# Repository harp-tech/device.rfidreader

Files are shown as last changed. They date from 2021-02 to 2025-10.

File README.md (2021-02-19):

# Harp RFID reader

RFID reader for 125KHz carriers.
Compible with glass capsules, buttons and cards (check pics folder).

# Licensing

The code, designs, documentation, and photos available in this repository is free: you can redistribute it and/or modify it under the terms of the used license.
Each subdirectory will contain a license or, possibly, a set of licenses if it involves both hardware and software. Check files named LICENSE.

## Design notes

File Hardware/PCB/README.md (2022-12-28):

## Licensing

The designs, documentation, and photos available in this repository are free: you can redistribute it and/or modify it under the terms of the used license.
Check file named LICENSE.

Copyright Filipe Carvalho 2021-2022

<br />This work is licensed under a <a rel="license" href="http://creativecommons.org/licenses/by-nc-sa/3.0/igo/">Creative Commons Attribution-NonCommercial-ShareAlike 3.0 IGO License</a>.

If your are interested in obtaining a license to sell this device, please contact filipe@oeps.tech

[1]: https://docs.google.com/spreadsheets/d/1aobmmEzBDethzIlrm1eg0eYkBqlyX3s9WbA9KgRwVQI/edit?usp=sharing

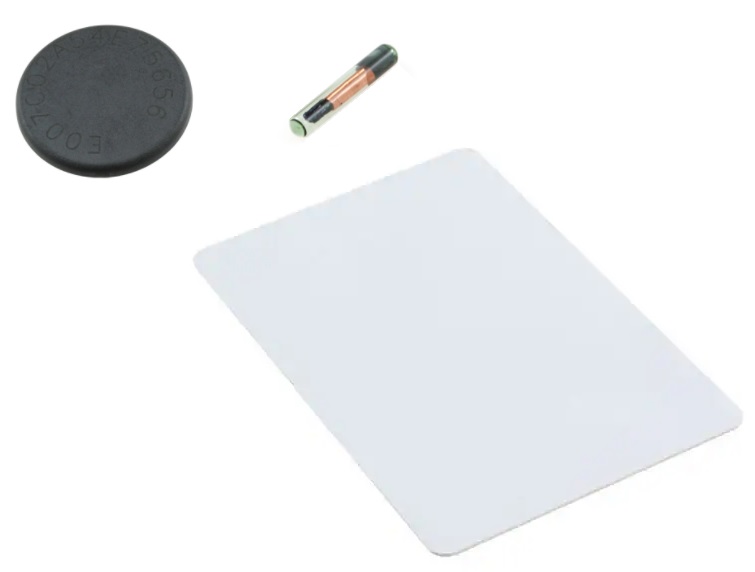
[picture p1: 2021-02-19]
Assets/compatible types of tags.jpg

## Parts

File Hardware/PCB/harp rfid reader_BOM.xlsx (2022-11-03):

Qty | Value | Package | Parts | MPN | Type | Distributor | Distributor PN
ASSEMBLY HOUSE
2 | 47pF | C0402 | C3, C4 | 04025A470JAT2A | SMD | Digikey | 478-1078-6-ND
1 | 4.7nF | C0402 | C1 | 885012205084 | SMD | Digikey | 732-12234-6-ND
11 | 100nF 50V X7R 10% | C0402 | C2, C6, C8, C9, C10, C12, C13, C14, C15, C16, C21 | CGA2B3X7R1H104K050BB | SMD | Digikey | 445-6899-6-ND
4 | 10uF 20% 16V X5R | C0603 | C5, C7, C11, C17 | EMK107BBJ106MA-T | SMD | Digikey | 587-3238-6-ND
3 | 100uF 20% 10V | CT3216 | C18, C19, C20 | TLJA107M010R1400 | SMD | Digikey | 478-5651-6-ND
1 | 39Ω 1/5watt 1% 0402 | R0402 | R7 | RCS040239R0FKED | SMD | Digikey | 541-10407-6-ND
5 | 1k | R0402 | R2, R3, R4, R6, R8 | CRCW04021K00FKED | SMD | Digikey | 541-1.00KLDKR-ND
1 | 10k | R0402 | R5 | CRCW040210K0FKED | SMD | Digikey | 541-10.0KLDKR-ND
1 | 1M | R0402 | R1 | CRCW04021M00FKED | SMD | Digikey | 541-1.00MLDKR-ND
1 | 40ohms 100MHz 1.5A 0805 SMD | L0805 | L1 | MI0805K400R-10 | SMD | Digikey | 240-2389-6-ND
1 | TRANS NPN 45V 0.5A | SC70-3 | Q1 | BC817-40W-7 | SMD | Digikey | BC817-40WDIDKR-ND
1 | MOSFET P-CH 60V 1.7A | SOT223 | Q2 | NTF2955T1G | SMD | Digikey | NTF2955T1GOSDKR-ND
4 | RED LED | LED0603 | TAG_B, TAG_T, STATE, OUT0 | 5975004407F | SMD | Digikey | 350-2950-6-ND
1 | Buzzers Transducer 3V 100mA 4kHz 78dB @ 3V |  | SP1 | SMT-0540-S-R | SMD | Digikey | 668-1060-6-ND
1 | USB to UART USB 2.0 | 28-SSOP | IC1 | FT232RL-REEL | SMD | Digikey | 768-1007-6-ND
1 | Ultra-Low-Noise LDO 3.3V 250mA | SOT-23-5 | IC2 | LP5907MFX-3.3/NOPB | SMD | Digikey | 296-38557-6-ND
1 | ATXMEGA32A4U | 44-TQFP | IC3 | ATXMEGA32A4U-A | SMD | Digikey | ATXMEGA32A4U-AURDKR-ND
1 | IC BUFFER NON-INVERT 5.5V | TSOP-5 | IC4 | M74VHC1GT126DT1G | SMD | Digikey | M74VHC1GT126DT1GOSDKR-ND
1 | 32 MHz CMOS | 4-SMD | OSC1 | O 32,0-JT32C-A-K-3,3-LF | SMD | Digikey | 1908-1044-6-ND
1 | CONN RCPT USB2.0 MINI |  | USB | UX60-MB-5S8 | SMD | Digikey | H2960DKR-ND
1 | CONN RCPT 5POS 0.1 GOLD SMD |  | U1 5POS | NPPN051BFLD-RC‎ | SMD | Digikey | ‎S5902-05-ND‎
1 | CONN RCPT 7POS 0.1 GOLD SMD |  | U1 7POS | ‎NPPN071BFLC-RC‎ | SMD | Digikey | ‎S5901-07-ND‎
1 | CONN Terminal block 2.54MM |  | OUT | 282834-2 | TH | Digikey | A98333-ND
POST-PRODUCTION
1 | RFID Reader ID-12LA (125 kHz) |  |  | ID-12LA | TH | SparkFun | SEN-11827
NOTES
 |  |  |  | Number of unique parts | 23
 |  |  |  | Number of SMD parts | 45
 |  |  |  | Number of TH parts | 1

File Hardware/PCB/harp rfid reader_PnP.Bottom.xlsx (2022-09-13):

C11 | 25.09 | 21.83 | 0 | 10uF | C0603
C12 | 23.55 | 2.46 | 270 | 100nF | C0402
C13 | 9.65 | 14.7 | 0 | 100nF | C0402
C14 | 19.72 | 20.88 | 90 | 100nF | C0402
C15 | 27.38 | 9.9 | 180 | 100nF | C0402
C16 | 16.8 | 3.37 | 270 | 100nF | C0402
C18 | 28.19 | 19.41 | 180 | 100uF | CT3216
C19 | 34.42 | 19.42 | 180 | 100uF | CT3216
C20 | 9.91 | 23.19 | 270 | 100uF | CT3216
C5 | 25.09 | 24.12 | 0 | 10uF | C0603
IC2 | 28.9 | 22.72 | 180 | LP5907MFX-3.3 | TSOT23-5
IC3 | 18.12 | 12.3 | 180 | ATXMEGA32A4U-AU | QFP80P1200X1200X120-44N
OSC1 | 20.29 | 2.38 | 0 | CNP-MISCELLANEOUS_OSCILLATOR | CNP-MISCELLANEOUS_OSCILLATOR_3.2X2.5
OUT0 | 40.55 | 19.45 | 270 |  | CHIP-LED0603
Q2 | 28.27 | 4.56 | 0 |  | SOT223
R3 | 25.6 | 11.16 | 90 | 1k | R0402
R4 | 21.79 | 23.86 | 0 | 1k | R0402
R7 | 34.83 | 8.8 | 180 | 75 >1/4W | R0402
SP1 | 33.92 | 13.45 | 0 | BUZZER-COIL_SMT-0540-S-R | BUZZER-COIL_SMT-0540-S-R
STATE | 25.6 | 13.45 | 180 |  | CHIP-LED0603
TAG_B | 18.74 | 23.86 | 90 |  | CHIP-LED0603

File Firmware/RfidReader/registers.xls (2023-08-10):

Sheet: registers
Has event. | When | Type | Array | Array Len. | Register Name | Desciption | Mask Type | Value | Name | Desciption
yes | When a tag is detected | U64 | no |  | TAG_ID_ARRIVED | Tag unique number was detected
yes | When a tag left the area | U64 | no |  | TAG_ID_LEAVED | Tag unique number left the antenna coverage area
yes | When it was trigger by TAG_MATCHx or OUT0_PERIOD | U8 | no |  | OUT | Writes to digital outputs | bit | (1<<0) | OUT0 | Digital output 0
no |  | U8 | no |  | NOTIFICATIONS | Enable the available notifications | bit | (1<<0) | BUZZER | Enables notification on buzzer
 |  |  |  |  |  |  | bit | (1<<1) | TOP_LED | Enables notification on top's LED
 |  |  |  |  |  |  | bit | (1<<2) | BOTTOM_LED | Enables notification on bottom's LED
no |  | U8 | no |  | TRIGGER_NOTIFICATIONS | Trigger the correspondent notifications | bit | (1<<0) | TRIG_BUZZER | Triggers notification on buzzer
 |  |  |  |  |  |  | bit | (1<<1) | TRIG_TOP_LED | Triggers notification on top's LED
 |  |  |  |  |  |  | bit | (1<<2) | TRIG_BOTTOM_LED | Triggers notification on bottom's LED
no |  | U16 | no |  | TIME_ON_BUZZER | Time the buzzer will be ON in milliseconds (minimum is 2) (sensitive to multiples of 2)
no |  | U16 | no |  | TIME_ON_LED_TOP | Time the top LED will be ON in milliseconds (minimum is 2) (sensitive to multiples of 2)
no |  | U16 | no |  | TIME_ON_LED_BOTTOM | Time the bottom LED will be ON in milliseconds (minimum is 2) (sensitive to multiples of 2)
no |  | U16 | no |  | BUZZER_FREQUENCY | Frequency of buzzer's notification (between 200 and 15000)
no |  | U16 | no |  | LED_TOP_BLINK_PERIOD | Blink period of top LED in milliseconds (minimum is 2) (sensitive to multiples of 2)
no |  | U16 | no |  | LED_BOTTOM_BLINK_PERIOD | Blink period of bottom LED in milliseconds (minimum is 2) (sensitive to multiples of 2)
no |  | U8 | no |  | RESERVED1 | Reserved
no |  | U8 | no |  | RESERVED2 | Reserved
no |  | U64 | no |  | TAG_MATCH0 | Notifies and sends TAG_ID event if the readed tag matches. Equal to 0 if not used.
no |  | U64 | no |  | TAG_MATCH1 | Notifies and sends TAG_ID event if the readed tag matches. Equal to 0 if not used.
no |  | U64 | no |  | TAG_MATCH2 | Notifies and sends TAG_ID event if the readed tag matches. Equal to 0 if not used.
no |  | U64 | no |  | TAG_MATCH3 | Notifies and sends TAG_ID event if the readed tag matches. Equal to 0 if not used.
no |  | U16 | no |  | TAG_MATCH0_OUT0_PERIOD | Defines the amount of time in ms that the digital output OUT0 will be at logic high when TAG_ID0 is detected
no |  | U16 | no |  | TAG_MATCH1_OUT0_PERIOD | Defines the amount of time in ms that the digital output OUT0 will be at logic high when TAG_ID1 is detected
no |  | U16 | no |  | TAG_MATCH2_OUT0_PERIOD | Defines the amount of time in ms that the digital output OUT0 will be at logic high when TAG_ID2 is detected
no |  | U16 | no |  | TAG_MATCH3_OUT0_PERIOD | Defines the amount of time in ms that the digital output OUT0 will be at logic high when TAG_ID3 is detected
no |  | U16 | no |  | TAG_ID_ARRIVED_PERIOD | When a tag is detected, OUT0 will be at high level for this amount of time in ms
no |  | U16 | no |  | OUT0_PERIOD | When writing to this register, the OUT0 will be on for this amount of time in ms

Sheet: meta data
who am I: | 2094
firmware major version: | 0
firmware minor version: | 2
hardware major version: | 1
hardware minor version: | 2
assembly version: | 0
device name: | RfidReader

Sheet: ios
Pin Name | PORT | Pin | Direction | Use Input | Out | Out default | Pull | Sense | Int. priority | Int. number | Desciption | Neg. Output
TAG_IN_RANGE | PORTC | 3 | input |  |  |  | tristate | both_edges | low | 0 | Tag in range
BUZZER | PORTD | 0 | output | yes | digital | 0 |  |  |  |  | Buzzer control | no
LED_DETECT_TOP | PORTD | 4 | output | yes | digital | 0 |  |  |  |  | Detect notification LED on top | no
LED_DETECT_BOTTOM | PORTC | 1 | output | yes | digital | 0 |  |  |  |  | Detect notification LED on bottom | no
OUT0 | PORTD | 7 | output | yes | digital | 0 |  |  |  |  | Digital output OUT0 | no
LED_OUT0 | PORTD | 6 | output | yes | digital | 0 |  |  |  |  | Notification of digital output OUT0 | no

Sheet: options
Array | Type | Array | Bits type | Direction | Use input | Pull | Sense | Int. priority | Int. number | Int. Mask | Out | Neg. Output
 |  |  |  | input | yes | up | both_edges | low | 0 |  | digital | yes
yes | U8 | yes | bit | output | no | down | rising_edge | med | 1 |  | wire_or | no
no | U16 | no | mask |  |  | tristate | falling_edge | high |  |  | wire_and
 | U32 |  | group_mask |  |  | busholder | low_level | off |  |  | wired_or_pull
 | U64 |  |  |  |  |  | no_interrupt |  |  |  | wired_and_pull
 | I8
 | I16
 | I32
 | I64
 | FLOAT

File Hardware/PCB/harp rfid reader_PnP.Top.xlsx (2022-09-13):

C1 | 3.2 | 19.77 | 90 | 4.7nF | C0402
C10 | 28.51 | 19.42 | 0 | 100nF | C0402
C17 | 24.83 | 15.92 | 270 | 10uF | C0603
C2 | 6.32 | 19.39 | 180 | 100nF | C0402
C21 | 40.55 | 9.99 | 0 | 100nF | C0402
C3 | 11.12 | 12.06 | 270 | 47pF | C0402
C4 | 11.05 | 15.18 | 90 | 47pF | C0402
C6 | 11.53 | 20.55 | 270 | 100nF | C0402
C7 | 9.14 | 22.35 | 270 | 10uF | C0603
C8 | 11.13 | 8.8 | 90 | 100nF | C0402
C9 | 23.26 | 16.13 | 270 | 100nF | C0402
IC1 | 17.07 | 13.45 | 0 | FT232RL | SSOP28
IC4 | 40.55 | 7.25 | 270 |  | SOT23-5
L1 | 6.89 | 22.38 | 270 | ??? | R0805
Q1 | 33.22 | 9.13 | 270 | BC817-40W | SOT323-BEC
R1 | 1.68 | 19.75 | 90 | 1M | R0402
R2 | 34.65 | 13.45 | 90 | 1k | R0402
R5 | 32.33 | 12.31 | 270 | 10k | R0402
R6 | 36.27 | 9.89 | 90 | 1k | R0402
R8 | 40.55 | 17.86 | 180 | 1k | R0402
TAG_T | 36.16 | 13.45 | 0 |  | CHIP-LED0603
USB | 8.78 | 13.45 | 270 |  | 240-0002-1
U1 5POS | 17.92 | 5.95 | 90
U1 7POS | 19.92 | 20.95 | 90

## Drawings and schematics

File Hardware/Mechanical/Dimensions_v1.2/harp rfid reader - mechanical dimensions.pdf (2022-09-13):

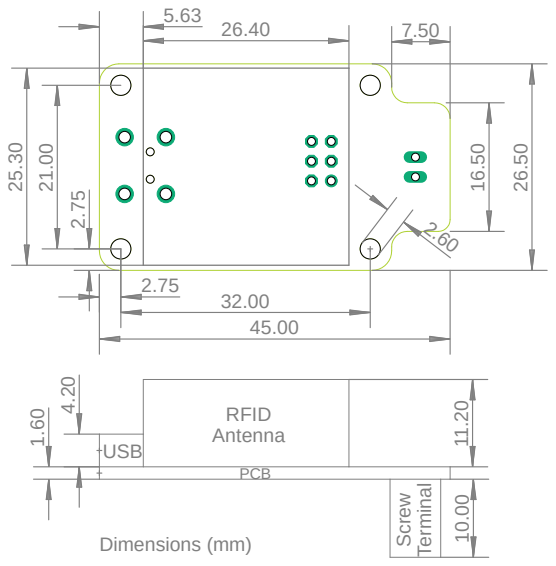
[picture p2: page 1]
Dimensions (mm); 2.60 1.604.20 10.00 11.20RFID; Antenna; Screw Terminal; USB; PCB ².75

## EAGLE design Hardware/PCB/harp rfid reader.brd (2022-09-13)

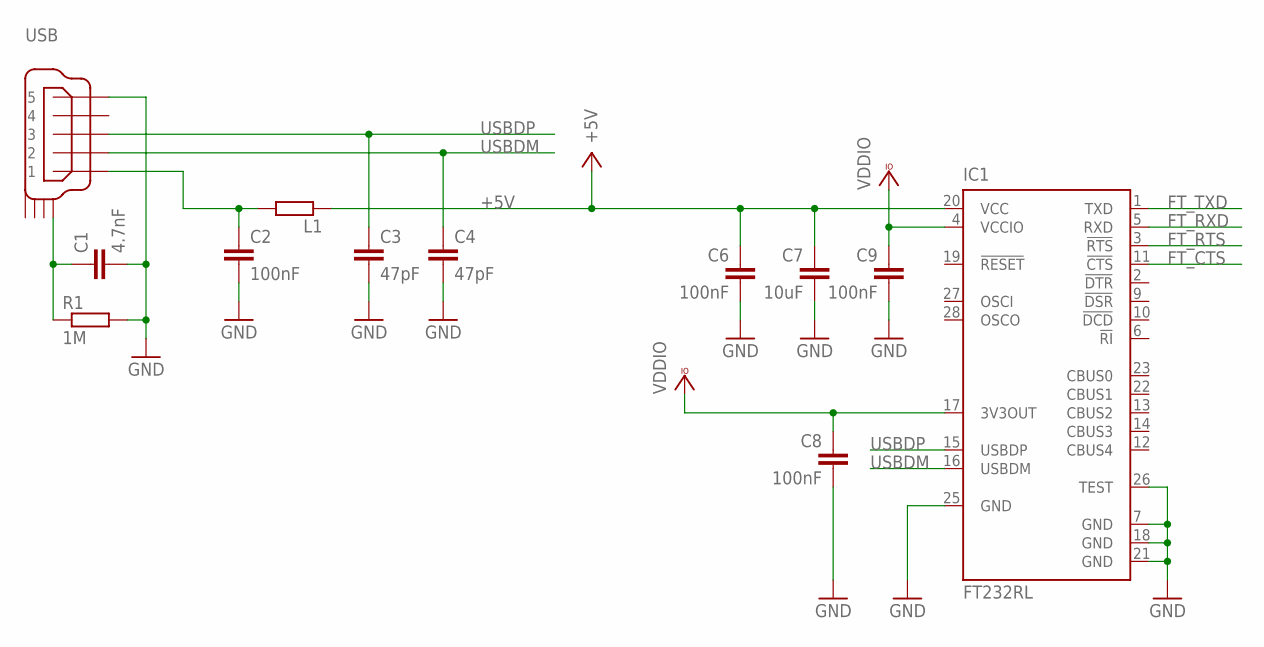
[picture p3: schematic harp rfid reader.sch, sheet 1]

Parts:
C1: 4.7nF; C0402
C2, C6, C8, C9: 100nF; C0402
C3, C4: 47pF; C0402
C7: 10uF; C0603
IC1: FT232RL; SSOP28
L1: ???; R0805
R1: 1M; R0402
USB: USB_MINI_B; 240-0002-1

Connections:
+5V: C6.1, C7.1, IC1.20 (VCC), L1.1; also elsewhere on the board
FT_CTS: IC1.11 (!CTS); also elsewhere on the board
FT_RTS: IC1.3 (!RTS); also elsewhere on the board
FT_RXD: IC1.5 (RXD); also elsewhere on the board
FT_TXD: IC1.1 (TXD); also elsewhere on the board
GND: C1.2, C2.2, C3.2, C4.2, C6.2, C7.2, C8.2, C9.2, IC1.7 (GND), IC1.18 (GND), IC1.21 (GND), IC1.25 (GND), IC1.26 (TEST), R1.2, USB.P$5 (5); also elsewhere on the board
unnamed: C1.1, R1.1, USB.SHIELD_1
unnamed: C2.1, L1.2, USB.P$1 (1)
USBDM: C4.1, IC1.16 (USBDM), USB.P$2 (2)
USBDP: C3.1, IC1.15 (USBDP), USB.P$3 (3)
VCCIO: C8.1, C9.1, IC1.4 (VCCIO), IC1.17 (3V3OUT); also elsewhere on the board

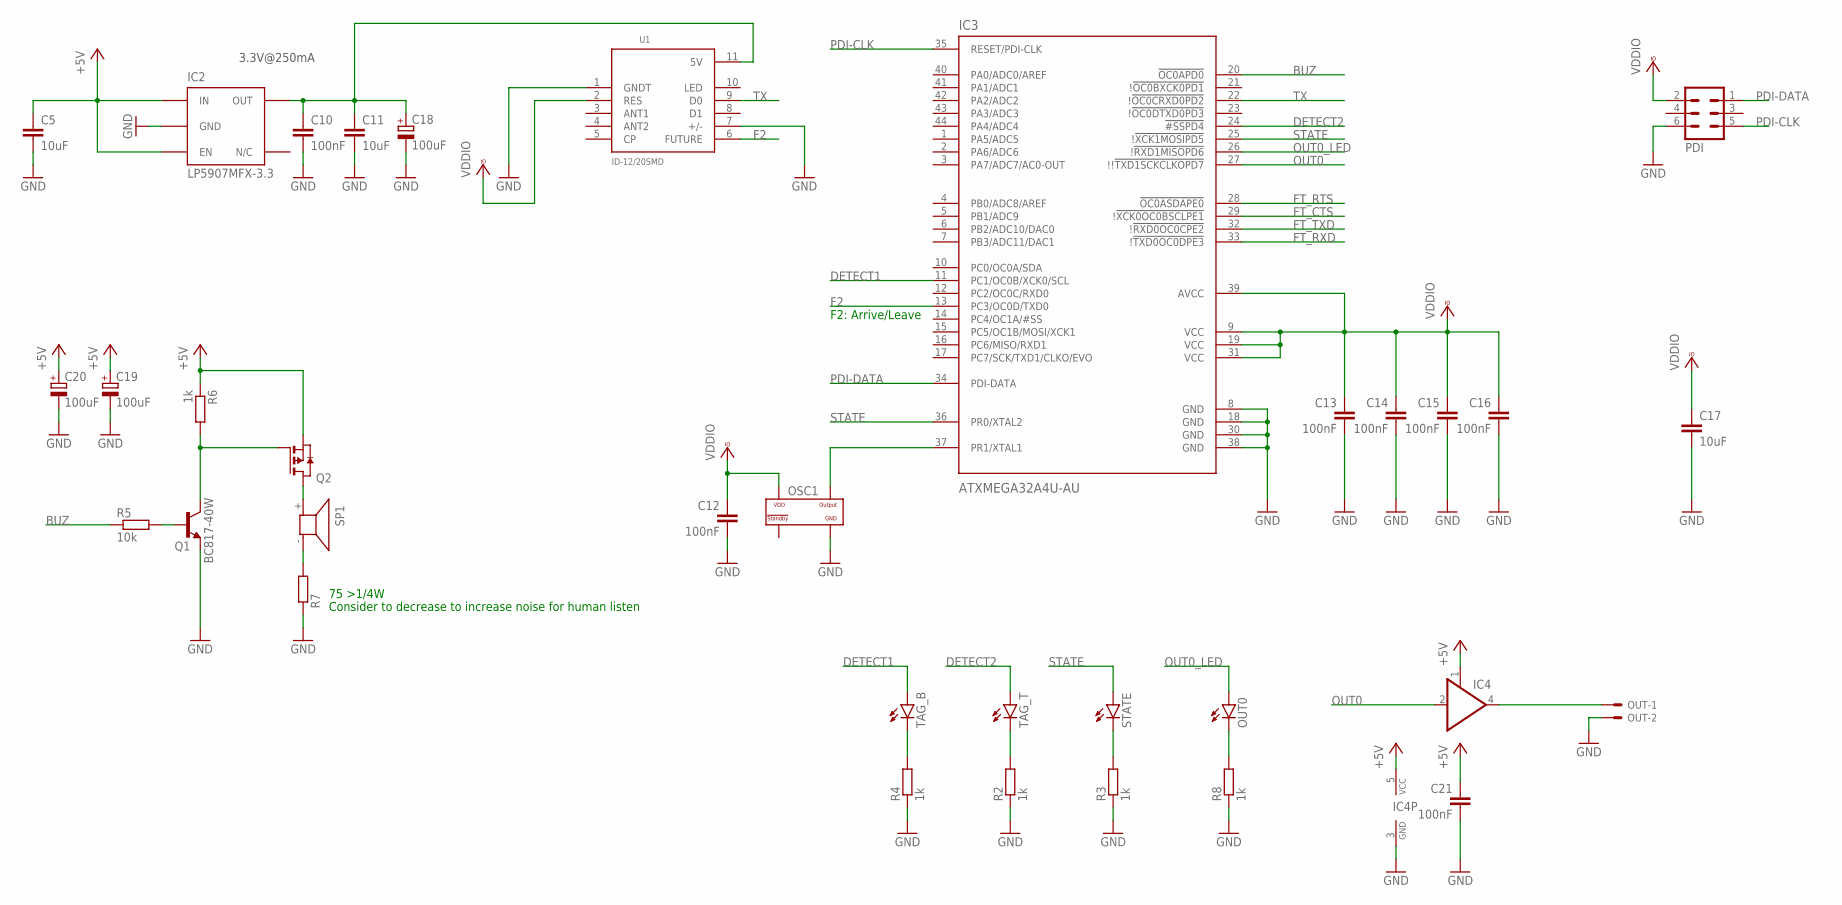
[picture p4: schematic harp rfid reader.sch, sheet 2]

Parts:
C5, C11, C17: 10uF; C0603
C10, C12, C13, C14, C15, C16, C21: 100nF; C0402
C18, C19, C20: 100uF; CT3216
IC2: LP5907MFX-3.3; TSOT23-5
IC3: ATXMEGA32A4U-AU; QFP80P1200X1200X120-44N
IC4: 74AHC1G126DBV; SOT23-5
OSC1: CNP-MISCELLANEOUS_OSCILLATOR; CNP-MISCELLANEOUS_OSCILLATOR_3.2X2.5
OUT: 22-23-2021
OUT0: LEDCHIP-LED0603; CHIP-LED0603
PDI: MA03-2
Q1: BC817-40W; SOT323-BEC
Q2: PMOSSOT223; SOT223
R2, R3, R4, R6, R8: 1k; R0402
R5: 10k; R0402
R7: 75 >1/4W; R0402
SP1: BUZZER-COIL_SMT-0540-S-R
STATE: LEDCHIP-LED0603; CHIP-LED0603
TAG_B: LEDCHIP-LED0603; CHIP-LED0603
TAG_T: LEDCHIP-LED0603; CHIP-LED0603
U1: ID-12/20SMD; ID-12_SMD

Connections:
+5V: C5.1, C19.+, C20.+, C21.1, IC2.1 (IN), IC2.3 (EN), IC4.1 (OE), IC4.5 (VCC), Q2.3 (S), R6.1; also elsewhere on the board
BUZ: IC3.20 (!OC0APD0), R5.1
BUZ_T: Q2.2 (D), Q2.4 (D), SP1.+
DETECT1: IC3.11 (PC1/OC0B/XCK0/SCL), TAG_B.A
DETECT2: IC3.24 (!#SSPD4), TAG_T.A
F2: IC3.13 (PC3/OC0D/TXD0), U1.6 (FUTURE)
FT_CTS: IC3.29 (!!XCK0OC0BSCLPE1); also elsewhere on the board
FT_RTS: IC3.28 (!OC0ASDAPE0); also elsewhere on the board
FT_RXD: IC3.33 (!!TXD0OC0DPE3); also elsewhere on the board
FT_TXD: IC3.32 (!!RXD0OC0CPE2); also elsewhere on the board
GND: C5.2, C10.2, C11.2, C12.2, C13.2, C14.2, C15.2, C16.2, C17.2, C18.-, C19.-, C20.-, C21.2, IC2.2 (GND), IC3.8 (GND), IC3.18 (GND), IC3.30 (GND), IC3.38 (GND), IC4.3 (GND), OSC1.P$2 (GND), OUT.2, PDI.6, Q1.E, R2.1, R3.1, R4.1, R7.1, R8.1, U1.1 (GNDT), U1.7 (+/-); also elsewhere on the board
unnamed: C10.1, C11.1, C18.+, IC2.5 (OUT), U1.11 (5V)
unnamed: R3.2, STATE.C
unnamed: R4.2, TAG_B.C
unnamed: R2.2, TAG_T.C
unnamed: OUT0.C, R8.2
unnamed: IC4.4 (O), OUT.1
unnamed: R7.2, SP1.-
unnamed: Q1.C, Q2.1 (G), R6.2
unnamed: Q1.B, R5.2
OSC1: IC3.37 (PR1/XTAL1), OSC1.P$3 (OUTPUT)
OUT0: IC3.27 (!!!TXD1SCKCLKOPD7), IC4.2 (I)
OUT0_LED: IC3.26 (!!RXD1MISOPD6), OUT0.A
PDI-CLK: IC3.35 (RESET/PDI-CLK), PDI.5
PDI-DATA: IC3.34 (PDI-DATA), PDI.1
STATE: IC3.25 (!!XCK1MOSIPD5), IC3.36 (PR0/XTAL2), STATE.A
TX: IC3.22 (!!OC0CRXD0PD2), U1.9 (D0)
VCCIO: C12.1, C13.1, C14.1, C15.1, C16.1, C17.1, IC3.9 (VCC), IC3.19 (VCC), IC3.31 (VCC), IC3.39 (AVCC), OSC1.P$4 (VDD), PDI.2, U1.2 (RES); also elsewhere on the board

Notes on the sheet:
3.3V@250mA
75 >1/4W
Consider to decrease to increase noise for human listen
F2: Arrive/Leave

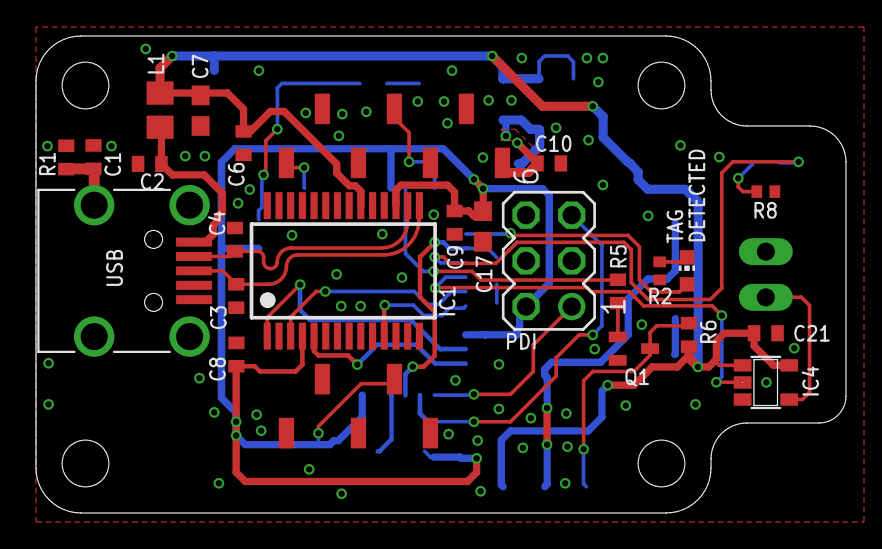
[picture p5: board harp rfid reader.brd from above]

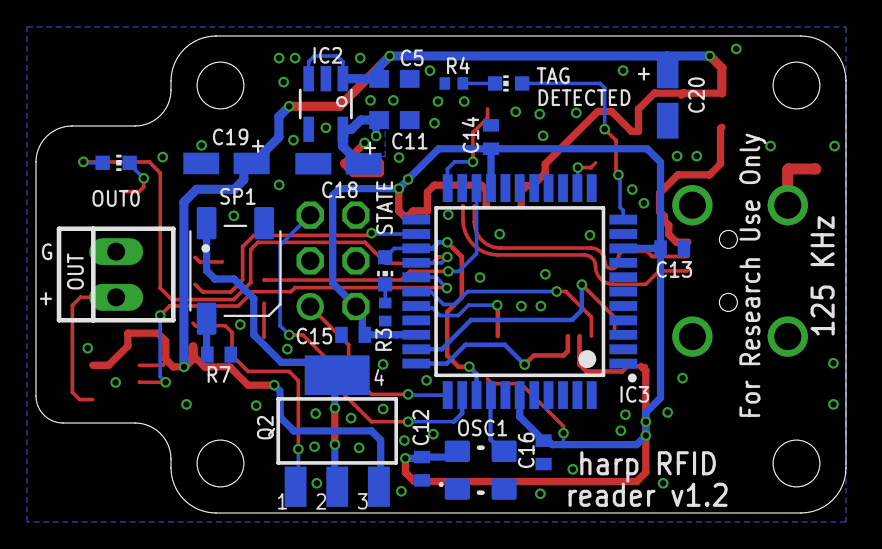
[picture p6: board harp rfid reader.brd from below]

Board: 2 copper layers, 45.0 x 26.5 mm, 46 parts (22 on the bottom side), 32 nets.

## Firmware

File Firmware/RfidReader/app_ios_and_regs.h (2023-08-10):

#ifndef _APP_IOS_AND_REGS_H_
#define _APP_IOS_AND_REGS_H_
#include "cpu.h"

void init_ios(void);
/************************************************************************/
/* Definition of input pins                                             */
/************************************************************************/
// TAG_IN_RANGE           Description: Tag in range

#define read_TAG_IN_RANGE read_io(PORTC, 3)     // TAG_IN_RANGE

/************************************************************************/
/* Definition of output pins                                            */
/************************************************************************/
// BUZZER                 Description: Buzzer control
// LED_DETECT_TOP         Description: Detect notification LED on top
// LED_DETECT_BOTTOM      Description: Detect notification LED on bottom
// OUT0                   Description: Digital output OUT0
// LED_OUT0               Description: Notification of digital output OUT0

/* BUZZER */
#define set_BUZZER set_io(PORTD, 0)
#define clr_BUZZER clear_io(PORTD, 0)
#define tgl_BUZZER toggle_io(PORTD, 0)
#define read_BUZZER read_io(PORTD, 0)

/* LED_DETECT_TOP */
#define set_LED_DETECT_TOP set_io(PORTD, 4)
#define clr_LED_DETECT_TOP clear_io(PORTD, 4)
#define tgl_LED_DETECT_TOP toggle_io(PORTD, 4)
#define read_LED_DETECT_TOP read_io(PORTD, 4)

/* LED_DETECT_BOTTOM */
#define set_LED_DETECT_BOTTOM set_io(PORTC, 1)
#define clr_LED_DETECT_BOTTOM clear_io(PORTC, 1)
#define tgl_LED_DETECT_BOTTOM toggle_io(PORTC, 1)
#define read_LED_DETECT_BOTTOM read_io(PORTC, 1)

/* OUT0 */
#define set_OUT0 set_io(PORTD, 7)
#define clr_OUT0 clear_io(PORTD, 7)
#define tgl_OUT0 toggle_io(PORTD, 7)
#define read_OUT0 read_io(PORTD, 7)

/* LED_OUT0 */
#define set_LED_OUT0 set_io(PORTD, 6)
#define clr_LED_OUT0 clear_io(PORTD, 6)
#define tgl_LED_OUT0 toggle_io(PORTD, 6)
#define read_LED_OUT0 read_io(PORTD, 6)


/************************************************************************/
/* Registers' structure                                                 */
/************************************************************************/
typedef struct
{
	uint64_t REG_TAG_ID_ARRIVED;
	uint64_t REG_TAG_ID_LEAVED;
	uint8_t REG_OUT;
	uint8_t REG_NOTIFICATIONS;
	uint8_t REG_TRIGGER_NOTIFICATIONS;
	uint16_t REG_TIME_ON_BUZZER;
	uint16_t REG_TIME_ON_LED_TOP;
	uint16_t REG_TIME_ON_LED_BOTTOM;
	uint16_t REG_BUZZER_FREQUENCY;
	uint16_t REG_LED_TOP_BLINK_PERIOD;
	uint16_t REG_LED_BOTTOM_BLINK_PERIOD;
	uint8_t REG_RESERVED1;
	uint8_t REG_RESERVED2;
	uint64_t REG_TAG_MATCH0;
	uint64_t REG_TAG_MATCH1;
	uint64_t REG_TAG_MATCH2;
	uint64_t REG_TAG_MATCH3;
	uint16_t REG_TAG_MATCH0_OUT0_PERIOD;
	uint16_t REG_TAG_MATCH1_OUT0_PERIOD;
	uint16_t REG_TAG_MATCH2_OUT0_PERIOD;
	uint16_t REG_TAG_MATCH3_OUT0_PERIOD;
	uint16_t REG_TAG_ID_ARRIVED_PERIOD;
	uint16_t REG_OUT0_PERIOD;
} AppRegs;

/************************************************************************/
/* Registers' address                                                   */
/************************************************************************/
/* Registers */
#define ADD_REG_TAG_ID_ARRIVED              32 // U64    Tag unique number was detected
#define ADD_REG_TAG_ID_LEAVED               33 // U64    Tag unique number left the antenna coverage area
#define ADD_REG_OUT                         34 // U8     Writes to digital outputs
#define ADD_REG_NOTIFICATIONS               35 // U8     Enable the available notifications
#define ADD_REG_TRIGGER_NOTIFICATIONS       36 // U8     Trigger the correspondent notifications
#define ADD_REG_TIME_ON_BUZZER              37 // U16    Time the buzzer will be ON in milliseconds (minimum is 2) (sensitive to multiples of 2)
#define ADD_REG_TIME_ON_LED_TOP             38 // U16    Time the top LED will be ON in milliseconds (minimum is 2) (sensitive to multiples of 2)
#define ADD_REG_TIME_ON_LED_BOTTOM          39 // U16    Time the bottom LED will be ON in milliseconds (minimum is 2) (sensitive to multiples of 2)
#define ADD_REG_BUZZER_FREQUENCY            40 // U16    Frequency of buzzer's notification (between 200 and 15000)
#define ADD_REG_LED_TOP_BLINK_PERIOD        41 // U16    Blink period of top LED in milliseconds (minimum is 2) (sensitive to multiples of 2)
#define ADD_REG_LED_BOTTOM_BLINK_PERIOD     42 // U16    Blink period of bottom LED in milliseconds (minimum is 2) (sensitive to multiples of 2)
#define ADD_REG_RESERVED1                   43 // U8     Reserved
#define ADD_REG_RESERVED2                   44 // U8     Reserved
#define ADD_REG_TAG_MATCH0                  45 // U64    Notifies and sends TAG_ID event if the readed tag matches. Equal to 0 if not used.
#define ADD_REG_TAG_MATCH1                  46 // U64    Notifies and sends TAG_ID event if the readed tag matches. Equal to 0 if not used.
#define ADD_REG_TAG_MATCH2                  47 // U64    Notifies and sends TAG_ID event if the readed tag matches. Equal to 0 if not used.
#define ADD_REG_TAG_MATCH3                  48 // U64    Notifies and sends TAG_ID event if the readed tag matches. Equal to 0 if not used.
#define ADD_REG_TAG_MATCH0_OUT0_PERIOD      49 // U16    Defines the amount of time in ms that the digital output OUT0 will be at logic high when TAG_ID0 is detected
#define ADD_REG_TAG_MATCH1_OUT0_PERIOD      50 // U16    Defines the amount of time in ms that the digital output OUT0 will be at logic high when TAG_ID1 is detected
#define ADD_REG_TAG_MATCH2_OUT0_PERIOD      51 // U16    Defines the amount of time in ms that the digital output OUT0 will be at logic high when TAG_ID2 is detected
#define ADD_REG_TAG_MATCH3_OUT0_PERIOD      52 // U16    Defines the amount of time in ms that the digital output OUT0 will be at logic high when TAG_ID3 is detected
#define ADD_REG_TAG_ID_ARRIVED_PERIOD       53 // U16    When a tag is detected, OUT0 will be at high level for this amount of time in ms
#define ADD_REG_OUT0_PERIOD                 54 // U16    When writing to this register, the OUT0 will be on for this amount of time in ms

/************************************************************************/
/* PWM Generator registers' memory limits                               */
/*                                                                      */
/* DON'T change the APP_REGS_ADD_MIN value !!!                          */
/* DON'T change these names !!!                                         */
/************************************************************************/
/* Memory limits */
#define APP_REGS_ADD_MIN                    0x20
#define APP_REGS_ADD_MAX                    0x36
#define APP_NBYTES_OF_REG_BANK              77

/************************************************************************/
/* Registers' bits                                                      */
/************************************************************************/
#define B_OUT0                             (1<<0)       // Digital output 0
#define B_BUZZER                           (1<<0)       // Enables notification on buzzer
#define B_TOP_LED                          (1<<1)       // Enables notification on top's LED
#define B_BOTTOM_LED                       (1<<2)       // Enables notification on bottom's LED
#define B_TRIG_BUZZER                      (1<<0)       // Triggers notification on buzzer
#define B_TRIG_TOP_LED                     (1<<1)       // Triggers notification on top's LED
#define B_TRIG_BOTTOM_LED                  (1<<2)       // Triggers notification on bottom's LED

#endif /* _APP_REGS_H_ */

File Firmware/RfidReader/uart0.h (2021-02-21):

#ifndef _UART0_H_
#define _UART0_H_

#include "cpu.h"


/************************************************************************/
/* UART definitions                                                     */
/************************************************************************/
#define UART0_RX_INT_LEVEL    INT_LEVEL_LOW
#define UART0_TX_INT_LEVEL    INT_LEVEL_LOW
#define UART0_CTS_INT_LEVEL   INT_LEVEL_LOW

#define UART0_RXBUFSIZ			64
#define UART0_TXBUFSIZ			8

#define UART0_UART				USARTD0	
#define UART0_PORT				PORTD
#define UART0_DATA				USARTD0_DATA
#define UART0_RX_pin			2
#define UART0_TX_pin			3

#define UART0_RX_ROUTINE_		ISR(USARTD0_RXC_vect, ISR_NAKED)
#define UART0_TX_ROUTINE_		ISR(USARTD0_DRE_vect, ISR_NAKED)


//#define UART0_USE_FLOW_CONTROL	// comment this line if don't use
#define UART0_RTS_PORT			PORTD
#define UART0_RTS_pin			6
#define UART0_CTS_PORT			PORTD
#define UART0_CTS_pin			7

#define UART0_CTS_ROUTINE_		ISR(PORTD_INT0_vect, ISR_NAKED)
#define UART0_CTS_INT_N			0

#define uart0_leave_interrupt /*return*/reti()

/************************************************************************/
/* Prototypes                                                           */
/************************************************************************/
#define disable_uart0_rx set_io(UART0_RTS_PORT, UART0_RTS_pin)
#define enable_uart0_rx	 clear_io(UART0_RTS_PORT, UART0_RTS_pin)

void uart0_init(uint16_t BSEL, int8_t BSCALE, bool use_clk2x);
void uart0_enable(void);
void uart0_disable();

void uart0_xmit_now(const uint8_t *dataIn0, uint8_t siz);
void uart0_xmit_now_byte(const uint8_t byte);
void uart0_xmit(const uint8_t *dataIn0, uint8_t siz);

void uart0_rcv_byte_callback(uint8_t byte);
bool uart0_rcv_now(uint8_t * byte);

#endif /* _UART0_H_ */

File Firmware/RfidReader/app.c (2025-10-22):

#include "hwbp_core.h"
#include "hwbp_core_regs.h"
#include "hwbp_core_types.h"

#include "app.h"
#include "app_funcs.h"
#include "app_ios_and_regs.h"

#include "uart0.h"

/************************************************************************/
/* Declare application registers                                        */
/************************************************************************/
extern AppRegs app_regs;
extern uint8_t app_regs_type[];
extern uint16_t app_regs_n_elements[];
extern uint8_t *app_regs_pointer[];
extern void (*app_func_rd_pointer[])(void);
extern bool (*app_func_wr_pointer[])(void*);

/************************************************************************/
/* Initialize app                                                       */
/************************************************************************/
static const uint8_t default_device_name[] = "RfidReader";

void hwbp_app_initialize(void)
{
    /* Define versions */
    uint8_t hwH = 1;
    uint8_t hwL = 2;
    uint8_t fwH = 1;
    uint8_t fwL = 4;
    uint8_t ass = 0;
    
   	/* Start core */
    core_func_start_core(
        2094,
        hwH, hwL,
        fwH, fwL,
        ass,
        (uint8_t*)(&app_regs),
        APP_NBYTES_OF_REG_BANK,
        APP_REGS_ADD_MAX - APP_REGS_ADD_MIN + 1,
        default_device_name,
        false,	// The device is not able to repeat the harp timestamp clock
        false,	// The device is not able to generate the harp timestamp clock
        3		// Default timestamp offset
    );
}

/************************************************************************/
/* Handle if a catastrophic error occur                                 */
/************************************************************************/
void core_callback_catastrophic_error_detected(void)
{
	timer_type0_stop(&TCC0);
	
	clr_BUZZER;
	clr_LED_DETECT_TOP;
	clr_LED_DETECT_BOTTOM;
}

/************************************************************************/
/* User functions                                                       */
/************************************************************************/
/* Add your functions here or load external functions if needed */

/************************************************************************/
/* Initialization Callbacks                                             */
/************************************************************************/
void core_callback_define_clock_default(void)
{
	/* Device don't have clock input or output */
}

void core_callback_initialize_hardware(void)
{
	/* Initialize IOs */
	/* Don't delete this function!!! */
	init_ios();
	
	/* Initialize hardware */
	uart0_init(12, 4, false);   // 1 Mb/s
	uart0_enable();
}

void core_callback_reset_registers(void)
{
	/* Initialize registers */
	app_regs.REG_NOTIFICATIONS = B_BUZZER | B_TOP_LED | B_BOTTOM_LED;
	app_regs.REG_TIME_ON_BUZZER = 500;				// 500 ms second
	app_regs.REG_TIME_ON_LED_TOP = 500;				// 500 ms second
	app_regs.REG_TIME_ON_LED_BOTTOM = 500;			// 500 ms second
	app_regs.REG_BUZZER_FREQUENCY = 1000;			// 1 KHz
	app_regs.REG_LED_TOP_BLINK_PERIOD = 100;		// 100 ms
	app_regs.REG_LED_BOTTOM_BLINK_PERIOD = 100;	// 100 ms
	app_regs.REG_TAG_MATCH0 = 0;
	app_regs.REG_TAG_MATCH1 = 0;
	app_regs.REG_TAG_MATCH2 = 0;
	app_regs.REG_TAG_MATCH3 = 0;
	app_regs.REG_TAG_MATCH0_OUT0_PERIOD = 0;
	app_regs.REG_TAG_MATCH1_OUT0_PERIOD = 0;
	app_regs.REG_TAG_MATCH2_OUT0_PERIOD = 0;
	app_regs.REG_TAG_MATCH3_OUT0_PERIOD = 0;
	app_regs.REG_TAG_ID_ARRIVED_PERIOD = 0;
}

void core_callback_registers_were_reinitialized(void)
{
	/* Update registers if needed */
	app_write_REG_BUZZER_FREQUENCY(&app_regs.REG_BUZZER_FREQUENCY);
	
}

/************************************************************************/
/* Callbacks: Visualization                                             */
/************************************************************************/
void core_callback_visualen_to_on(void)
{
	/* Update visual indicators */
	
}

void core_callback_visualen_to_off(void)
{
	/* Clear all the enabled indicators */
	clr_LED_DETECT_TOP;
	clr_LED_DETECT_BOTTOM;
	clr_LED_OUT0;
}

/************************************************************************/
/* Serial RX                                                            */
/************************************************************************/
uint8_t rxbuff_pointer = 0;
extern uint8_t rxbuff_uart0[];

uint16_t out0_timeout_ms = 0;

/*
[02]000C845A994B
[03][02]000C845A994B
[03][02]0077D1AD000B
[03][02]000C845A77A5
[03][02]021000001705
[03][02]000C845A7EAC
[03]

[02]000C845A79AB
[03][02]000C845A79AB
[03]

STX (02h) DATA (10 ASCII) CHECK SUM (2 ASCII) CR LF ETX (03h)

*/

uint16_t buzzer_time_on = 0;
uint16_t top_led_time_on = 0;
uint16_t bottom_led_time_on = 0;
uint16_t top_led_period = 0;
uint16_t bottom_led_period = 0;

bool stop_buzzer;

extern uint8_t buzzer_prescaler;
extern uint16_t buzzer_target_count;

bool id_event_was_sent = false;
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

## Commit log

2021-02-19 Added first PCB files.
    [harp rfid reader v1.0 BOM.xlsx, harp rfid reader v1.0.brd, harp rfid reader v1.0.sch]
2021-02-19 Added compatible devices.
2021-02-21 Added first firmware files.
    [registers.xls]
2021-02-21 Increased oscillator and buzzer pads.
    [harp rfid reader v1.0.brd, harp rfid reader v1.0.sch]
2021-02-21 Replaced microcontroller.
    [harp rfid reader v1.0 BOM.xlsx]
2021-02-26 Updated firmware.
    [xmega_usart_calc.xls]
2021-02-26 Correct footprints of buzzer and oscillator.
    [harp rfid reader v1.0.brd]
2021-05-03 Minor PCB corrections.
    [harp rfid reader BOM.xlsx, harp rfid reader v1.0 BOM.xlsx, harp rfid reader.brd, harp rfid reader.sch]
2021-05-03 Added 3 new capacitors.
    [harp rfid reader BOM.xlsx, harp rfid reader.brd, harp rfid reader.sch]
2022-05-06 Corrected STATE and DETECT lines and increased LED resistors.
    [harp rfid reader BOM.xlsx, harp rfid reader.brd, harp rfid reader.sch]
2022-05-06 Remapped TOP LED to PC1.
    [registers.xls]
2022-05-08 Added new event and renamed reserved registers.
    New event: (REG 33 U64) TAG_ID_LEAVED -> When tag leaves the detection zone.
    [registers.xls]
2022-05-09 Increased hardware version to match the current PCB version.
2022-05-25 Added a digital output.
    [harp rfid reader BOM.xlsx, harp rfid reader.brd, harp rfid reader.sch]
2022-09-13 Added fabrication files and updated BOM.
    [harp rfid reader BOM.PnP.Bottom.xlsx, harp rfid reader BOM.PnP.Top.xlsx, harp rfid reader BOM.xlsx]
2022-09-13 Added mechanical dimensions.
    [harp rfid reader BOM.xlsx, harp rfid reader.brd]
2022-09-13 Added more details to mechanical dimensions file.
    [harp rfid reader.brd]
2022-09-13 Minor BOM correction.
    [harp rfid reader BOM.xlsx]
2022-11-03 Minor corrections.
    [harp rfid reader BOM.xlsx]
2022-12-07 Added new registers to handle the digital output.
    [registers.xls]
2022-12-07 Ability to turn LEDs off.
2022-12-27 Refactored hardware files.
    [harp rfid reader.brd, harp rfid reader.sch, harp rfid reader_BOM.PnP.Bottom.xlsx, harp rfid reader_BOM.PnP.Top.xlsx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]
2022-12-27 Renamed files.
    [harp rfid reader_PnP.Bottom.xlsx, harp rfid reader_PnP.Top.xlsx]
2023-04-18 Add first draft of device schema
2023-04-19 Change device name
2023-04-21 Fixed bad bitmasks.
    The notification and trigger bitmasks where corrected.
    [registers.xls]
2023-06-02 Update `Device` classes to new schema
2023-08-10 Add minor clarifications to device schema
2023-09-04 Added excel file explaining how to parse the ID.
    [ID-12LA-ISO parse.xlsx]
